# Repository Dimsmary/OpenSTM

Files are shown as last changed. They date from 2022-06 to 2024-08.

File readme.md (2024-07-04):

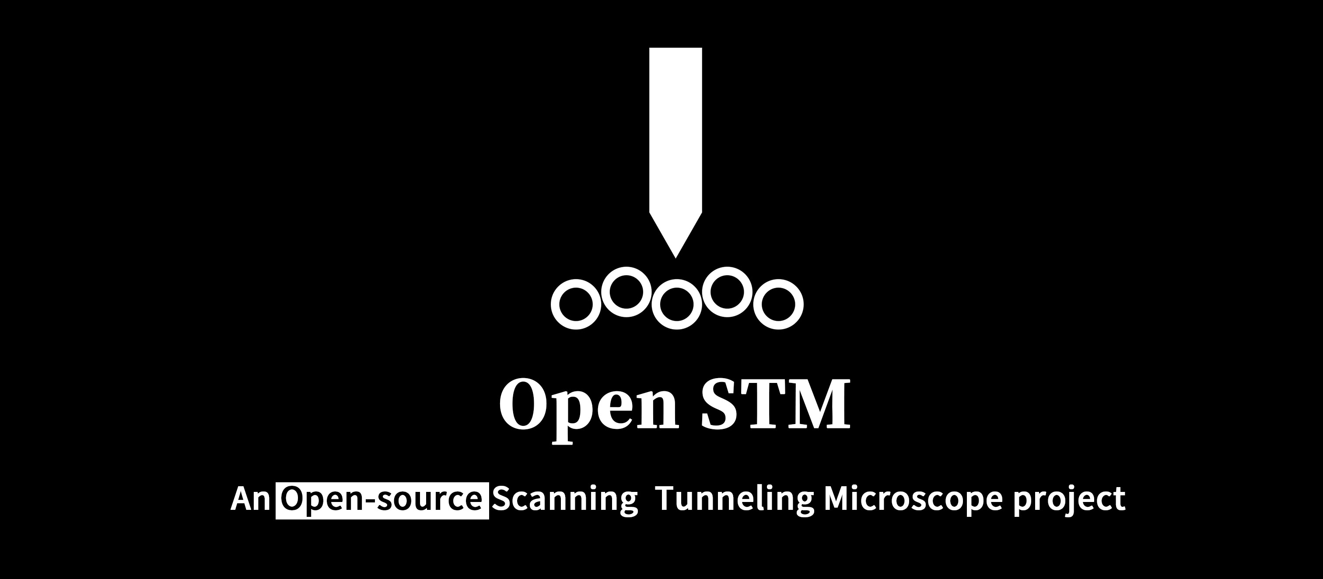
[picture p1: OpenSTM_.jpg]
OpenSTM_


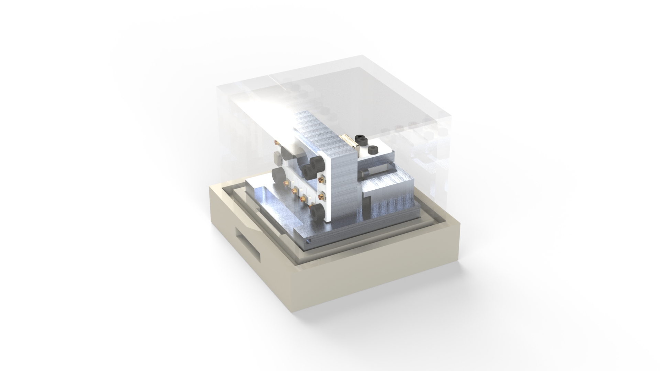
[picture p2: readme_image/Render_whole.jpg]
Render_whole


**[中文](readme.md) | [English](readme_eng.md)**

- [简介](#简介)
- [分支](#分支)
- [开源文件结构介绍](#开源文件结构介绍)
- [开发技术文档](#开发技术文档)
- [版本发布命名规则](#版本发布命名规则)
- [已发布的STM方案版本](#已发布的stm方案版本)
  - [<u>Release OpenSTM v1.0.0</u>](#urelease-openstm-v100u)
  - [<u>Release OpenSTM v2.0.0</u>](#urelease-openstm-v200u)
  - [<u>Release OpenSTM v3.0.0</u>](#urelease-openstm-v300u)
- [目前取得的成果](#目前取得的成果)
  - [隧穿距离-电流曲线](#隧穿距离-电流曲线)
  - [热解石墨（HOPG）的偏压-电流曲线](#热解石墨hopg的偏压-电流曲线)
  - [热解石墨（HOPG）原子成像](#热解石墨hopg原子成像)
- [联系我](#联系我)
- [赞助](#赞助)
- [开发记录](#开发记录)
- [致谢](#致谢)
- [参考工程](#参考工程)
- [主要参考文献](#主要参考文献)

# 简介

嗨，本项目是一个旨在通过DIY来搭建一个原子级扫描隧道显微镜。  

2022年6月，本项目已经成功测量了隧穿距离-电流曲线、热解石墨（HOPG）的偏压-电流曲线以及样品无尺寸定性成像。  

2023年5月，本项目成功扫描出热解石墨（HOPG）的碳原子。  

目前项目已经在科学开源硬件期刊《HardwareX》上发表，构建细节可参考论文内容。论文DOI：https://doi.org/10.1016/j.ohx.2023.e00504

# 分支

本仓库目前创建了两个分支，即[主分支](https://github.com/Dimsmary/OpenSTM/tree/main)(main)以及[文档分支](https://github.com/Dimsmary/OpenSTM/tree/Ref-Document)(Ref-Document)。主分支中放置了源代码等工程设计文件，文档分支放置了开发过程中参考的文档资料。之所以将这两部分分离是因为文档文件体积过于庞大所导致的。

# 开源文件结构介绍

- 3DModels

  包括**外壳设计文件**以及**CNC加工所需的STEP文件** 。

- Docs

  该目录下的文档包括了**项目概要**以及**显微镜构建指南**。
  
- Hardware
  
  包括使用ESP32 IDF编写的**单片机程序工程文件**（使用Platform IO），以及对应**固件**。
  注意！Platform IO的Platforms-Espressif 32版本应选择6.0.0，否则可能无法通过编译。

- PCB

  嘉立创EDA绘制的**PCB文件**，需要使用嘉立创EDA专业版打开。或直接在OSHW-Hub在线浏览（详见电路部分），移步[OSHWHUB](https://oshwhub.com/Dimsmary/4ieRpV8S00kGn1MTpsc4MyZat8MwQPzn)，点击右上方的“编辑器打开”。

- PythonScript  
  显微镜的上位机程序，具体使用方法参考**显微镜构建指南**。

# 开发技术文档

文档已发布在Arxiv: https://arxiv.org/abs/2310.05413, 你也可以在doc文件夹中寻找到。

# 版本发布命名规则

截至2023/10，目前已公布了三个不同机械结构的STM方案 ，其中V3.0.0版本已经可以实现STM的基本功能。

本项目将参考软件发行的方式，在STM方案更新后，采用Release的方式对方案进行发布，每次发布的STM方案版本号命名规则如下：

版本号以**A.B.C**式命名，当方案机械结构存在重构时，A将发生变化。在方案的电路、软件、机械结构存在较大的修改时，B将发生变化。当方案存在细微修改时，C将发生变化。

以1.0.0为例，该版本号即代表第一代机械结构的STM设计方案。

# 已发布的STM方案版本

## [<u>Release OpenSTM v1.0.0</u>](https://github.com/Dimsmary/OpenSTM/releases/tag/v1.0.0)

这是初代STM方案，机械结构采用两块铝板搭建：[<u>你，亲眼看过原子吗？ - 哔哩哔哩</u>](https://www.bilibili.com/video/BV1Jr4y1v7gq)  

方案较为简单，没有取得能够用于分析的实验结果，但后续方案的搭建基于本初代方案进行搭建，本版本的方案仅供参考，暂不提供详细的文档资料。  
发布的方案文件包括了：

- 3D模型文件（SolidWorks）
- Arduino程序：用于控制STM的ESP32单片机控制程序（采用LVGL进行交互）、基于MPU9250的震动探测程序，均采用Arduino+Platform IO进行开发
- PCB及原理图
- 用于测量干涉条纹的Python脚本
- LTSpice对电源芯片的仿真文件

## [<u>Release OpenSTM v2.0.0</u>](https://github.com/Dimsmary/OpenSTM/releases/tag/v2.0.0)

该版本方案为第二代显微镜结构：  [<u>耗时九个月，我可能来到了纳米尺度...... - 哔哩哔哩</u>](https://www.bilibili.com/video/BV1eB4y1S7u8)

该方案的结构能够测量：

- 隧穿距离-电流曲线
- 扫描隧道谱（STS）

v2.0.0.zip内含的文件包括：

- 3DModel：SolidWorks绘制的3D模型文件、CNC加工所需的STEP文件
- PCB：立创EDA专业版绘制的原理图、PCB文件
- Software：在Arduino文件夹下，包含ESP32单片机的控制程序、ATMEGA 328P单片机的控制程序。在Python文件夹下，包含了上位机控制软件、图像转换程序

## [<u>Release OpenSTM v3.0.0</u>](https://github.com/Dimsmary/OpenSTM/releases/tag/v3.0.0)

第三代扫描隧道显微镜，功能基本完善的一个版本，能够完成基本的曲线测量以及HOPG原子成像。
视频：https://www.bilibili.com/video/BV1TN411r7jG
复刻论文手稿：https://arxiv.org/abs/2310.05413
详细内容请参考手稿。

# 目前取得的成果

## 隧穿距离-电流曲线

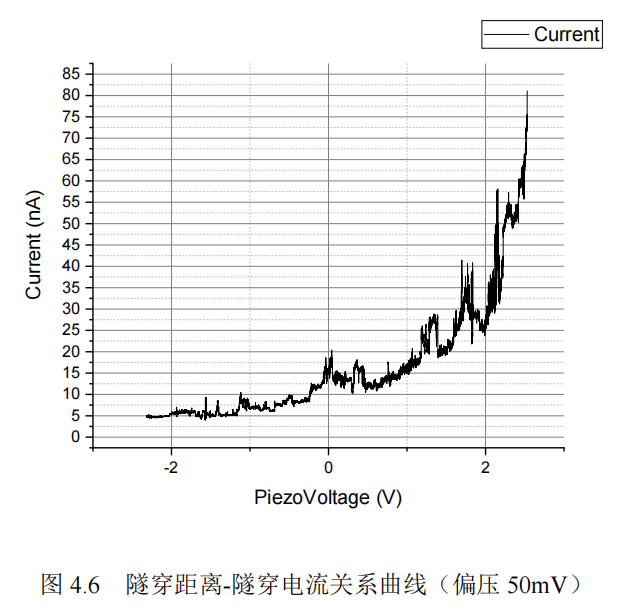
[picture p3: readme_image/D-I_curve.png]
D-I_curve
  

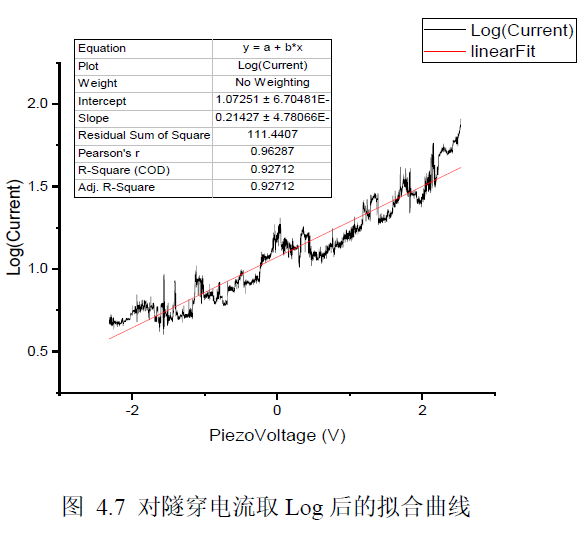
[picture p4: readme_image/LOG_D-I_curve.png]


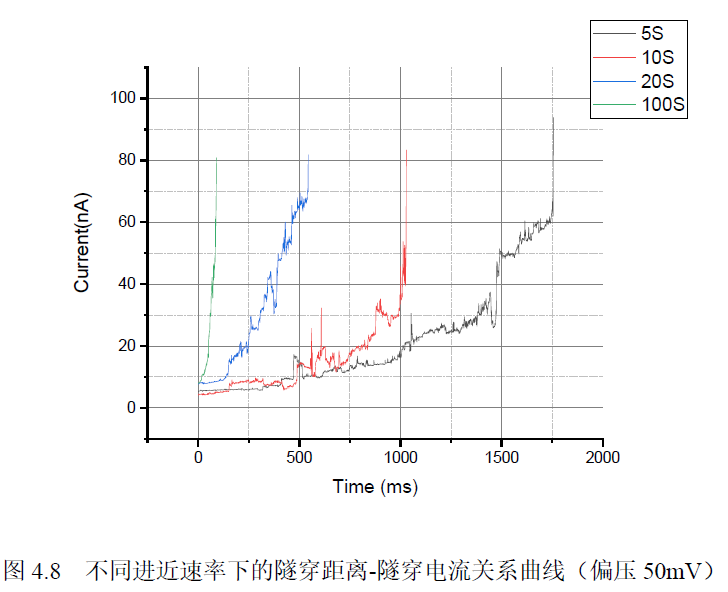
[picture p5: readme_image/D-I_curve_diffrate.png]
D-I_curve_diffrate
  

## 热解石墨（HOPG）的偏压-电流曲线

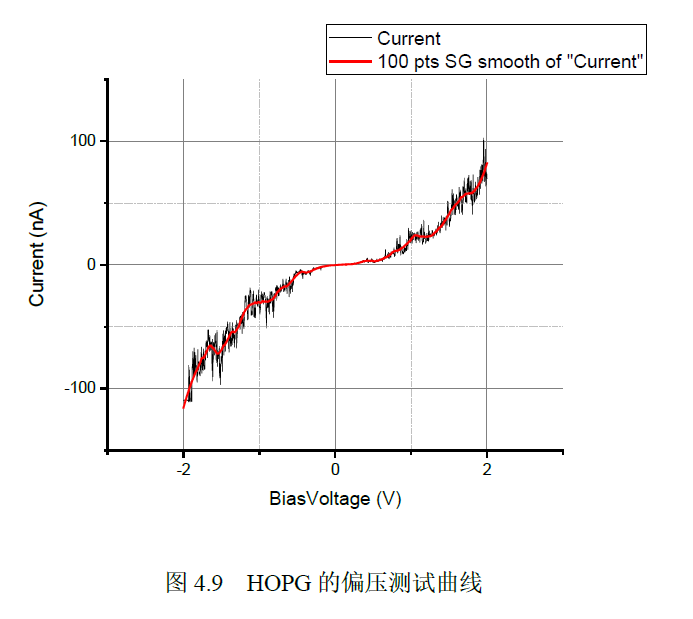
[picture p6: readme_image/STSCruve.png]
STSCruve


## 热解石墨（HOPG）原子成像

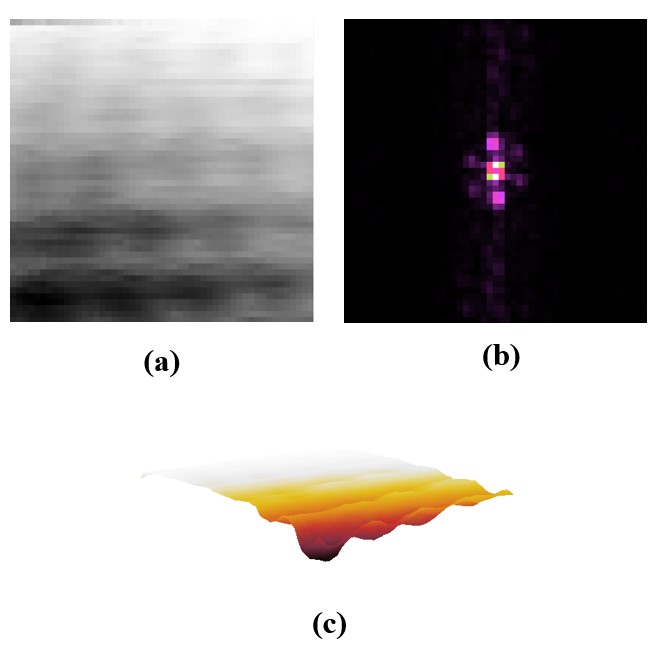
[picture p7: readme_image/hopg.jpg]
hopg


# 联系我

  如果你也想制作一个STM显微镜，或者对我有什么建议的话，可以在此页面提交Issue。

# 赞助

如果你喜欢本项目，欢迎在爱发电对我进行赞助：https://afdian.net/a/dimsmary

赞助可获得概述中文版一份。（虽然复刻指南已经发布在了Arxiv，但这里还是有一份中文省流版；
这份文档是对项目的一个概述，相较于readme更为详细，但复刻还是要参考Arxiv论文）

# 开发记录

- 2021/11
  
  不稳定隧穿

- 2022/1/11
  
  开源页面提交

- 2022/1/18
  
  减震台下加装了<网球>，减震效果拔群

- 2022/2/05
  
  1）系统模拟部分供电改为9V电池供电，数字部分继续使用开关电源。  
  2）ADP5070不工作了，奶奶的！为什么。  
  3）在《 Construction of a scanning tunneling microscope for imaging of carbon nanotubes》P35中发现隧穿电流应在100pA - 10nA，按照现有运放的倍数应该关注1V以内的信号，之前看样子搞错了。  
  4）OPA627的 ~~开环电压增益有120dB，~~ 输入偏置电流1pA，讲道理用100MΩ的反馈电阻应该是可行的？  

- 2022/2/16  
  
  对运放的输入输出特性进行了测试，证明前级隧道电流放大电路是可行的。

- 2022/3/14  
  
  1）CNC加工的新结构加工完成  
  2）摒弃LVGL与显示屏作为控制系统  

- 2022/3/21  
  
  使用了新的结构系统、电路、控制系统进行了隧穿电流进近测试：  
  1）隧穿电流初步稳定，能够维持十几秒。  
  2）通过八个点的采样测试隧穿电流-压电陶瓷形变曲线发现基本符合指数特征。  
  3）确认并不需要非常复杂的减震系统。  
  4）基本确认之前出现的输出跳动现象为热膨胀的失配。

- 2022/4/12  
  
  1）在对进近机械结构中的步进电机进行热隔离调整后，隧穿电流已非常稳定，能够维持至少30分钟。  
  2）对新的隧穿曲线进行分析，发现电流-压电陶瓷形变关系并不只是单纯的指数关系，结合老师给出的意见，怀疑有其他函数复合。初步怀疑为针尖与样品间形成的电容器导致的。  
  3）完善了细进近控制算法，现在可以点击开始进近之后去打几把极地大乱斗。  
  4）模拟部分供电由9V电池供电更换为3S锂聚合物电池供电。

- 2022/4/20  
  完成恒高模式下的STM图像扫描，并经过重复性实验验证，但无法确定图像尺度以及成像内容的完全可靠。

- 2022/5/01  
  攥写毕业设计论文。

- 2022/5/04  
  毕业设计论文攥写完成70%，开始编写恒流扫描算法。  

- 2022/6/16  
  第二代显微镜开源资料公布  

- 2022/10/21
  
  开始设计粘滑压电马达

- 2022/10/26
  
  完善技术文档
  
- 2023/1/4
  第三代电路、机械结构重构完成，粘滑压电马达设计完成，进入调试阶段（目前未发布，待验证后发布）。
  
  （1）电路电源方面：重构后的电路采用ADP5070搭配低噪声LDO的方案提供多个电源轨道（双±12V、5V），ADP5070采用紫米35W双C口电源适配器进行5V供电（原因在于该电源纹波极低，峰峰值在13mV左右，呈现为锯齿状）。
  
  （2）PCB板层设计方面：新一代电路板分为三块：电源板、MCU板、控制板。电源线在板之间采用同轴信号线连接，数据线采用IDC排线连接。
  
  （3）电路改进方面：MCU板继续沿用ESP32作为控制器，但模组型号更新为ESP32-S3，并留有WIFI天线挖槽，为日后升级做准备。控制板沿用第二代大部分设计保持不变，继续使用AD5761+OPA2227的方案对扫描头进行控制，但由于压电滑台的引入，控制板额外添加了AD8761作为对样品施加偏压的DAC，原本用于施加偏压的DAC现用于控制压电滑台。
  
  （4）机械结构设计方面：新一代机械结构整体尺寸缩小，并引入了粘-滑压电滑台进行粗进近（参考文章《Open-source XYZ nanopositioner for high-precision analytical applications》），并对前级放大器进行了金属全包裹屏蔽，进一步降低噪声耦合。
  
- 2023/1/18

  MCU模组更换为ESP32-WROOM-32E，S3模组的编译出现了一些问题，资料较少暂时无法解决。
  
  另外，为了提升MCU的效率，将开发框架从Arduino变更为ESP-IDF（从简单的GPIO翻转代码中发现，Platform IO + Arduino速度为800Khz，Arduino IDE为1.2Mhz，Platform IO + ESP-IDF为1.44Mhz）。
  
- 2023/2/12
  
  第三代电路、机械结构修改、验证完成。
  
  目前正在重构上位机、控制程序，截止目前已实现探针进近的PID控制，电流相较于上一代设计更加稳定，温漂问题得到很大程度改善。
  
- 2023/03/31
  
  1）发现了一些在压电滑台组装时遇到的问题：虽然压电滑台组装难度不高，但滑台在安装时需要与施加压力的磁铁保持一定程度的平行，否则压电滑台将无法长距离工作。
  
  2）拟设计两种压电滑台结构以适配不同形状的压电陶瓷
  
  3）软件完成D-I曲线测试以及偏压测试功能
  
- 2023/05/02
  
  1）完成了对HOPG的扫描，可以观察到碳原子模糊的轮廓。
  
  2）发现了一个有趣的现象：在探测HOPG样品的过程中，探针接近完成后的隧穿电流将会产生波动（环境振动引起），若此时的探针锐度达到了原子级分辨率，隧穿电流的波动曲线将会被耦合进一个类正弦波的曲线，并且在撞针后，这个耦合将消失（确定不为市电干扰，其波动周期为1.4ms左右，且在撞针后会消失）。
  
  我认为这是因为探针在进入隧穿距离之后，在环境振动的带动下，探针的X/Y轴将随着振动而移动，形成“扫描”的效果，碳原子表面的起伏将导致电流的周期性变化。
  
- 2023/05/03
  
  观察到HOPG上碳原子清晰的轮廓

- 2023/10/10

  三代机HardwareX手稿发布在Arxiv上：https://arxiv.org/abs/2310.05413

# 致谢

**五邑大学以及五邑大学的老师们**

**深圳嘉立创科技集团股份有限公司**

**Jürgen Müller**

**Daniel Berard的STM开源工程**

**John D. Alexander的STM开源工程**

**中国科学院光电技术研究所**

**所有为本项目提供建议的哔哩哔哩朋友**

# 参考工程

[1] John Alexander: STM Project, http://web.archive.org/web/20121107205242/http://www.geocities.com/spm_stm/Project.html

[2] Dan Berard: Home-Built STM, https://dberard.com/home-built-stm/

[3] Jürgen Müller: Homebrew STM, http://www.e-basteln.de/other/stm/overview/

[4] NanoSurf: NaioSTM, https://www.nanosurf.com/en/products/naiostm-stm-for-nanoeducation

# 主要参考文献 

[1].  Binnig G, Rohrer H. Scanning tunneling microscope: U.S. Patent 4,343,993[P]. 1982-8-10.

[2].  Besocke K. An easily operable scanning tunneling microscope[J]. Surface Science, 1987, 181(1-2): 145-153.

[3].  Ellis M D. Construction of a scanning tunneling microscope for imaging of carbon nanotubes[D]. Texas Tech University, 1998.

[4].  Rogers B L, Shapter J G, Skinner W M, et al. A method for production of cheap, reliable pt–ir tips[J]. Review of Scientific Instruments, 2000, 71(4): 1702-1705.

[5].  王琦. 高稳定扫描隧道显微镜的研制与应用[D].  中国科学技术大学,2014.

[6].  Petersen J P, Kandel S A. Circuit design considerations for current preamplifiers for scanning tunneling microscopy[J]. 2017.

[7].  Lounis S. Theory of scanning tunneling microscopy[J]. arXiv preprint arXiv:1404.0961, 2014.

[8].  Purdue University. TEM Pictures of STM Tips[EB/OL]. 2002[2022-9-20]. https://www.physics.purdue.edu/nanophys/uhvstm/tip.html.

[9].  Bai C. Scanning tunneling microscopy and its application[M]. Springer Science & Business Media, 2000.

[10].  Nasrollahzadeh M, Sajadi M S, Atarod M, et al. An introduction to green nanotechnology[M]. Academic Press, 2019:199-322.

[11].  Baird D, Shew A. Probing the history of scanning tunneling microscopy[J]. Discovering the nanoscale, 2004, 2: 145-156.

[12].  Merzbacher E. Quantum mechanics[M]. Jones & Bartlett Publishers, 1961.

[13].  曾谨言. 量子力学导论[M]. 第二版. 北京大学出版社, 2001.

[14].  Grafstrom S, Kowalski J, Neumann R. Design and detailed analysis of a scanning tunnelling microscope[J]. Measurement Science and Technology, 1990, 1(2): 139.

[15].  Nam A J, Teren A, Lusby T A, et al. Benign making of sharp tips for STM and FIM: Pt, Ir, Au, Pd, and Rh[J]. Journal of Vacuum Science & Technology B: Microelectronics and Nanometer Structures Processing, Measurement, and Phenomena, 1995, 13(4): 1556-1559.

[16].  Hahn J R, Hong Y A, Kang H. Electron tunneling across an interfacial water layer inside an STM junction: tunneling distance, barrier height and water polarization effect[J]. Applied Physics A, 1998, 66(1): S467-S472.

[17]. Woo D H, Choi E M, Yoon Y H, et al. Current–distance–voltage characteristics of electron tunneling through an electrochemical STM junction[J]. Surface science, 2007, 601(6): 1554-1559.

[18]. Alexander J D, Tortonese M, Nguyen T. Atomic force microscope with integrated optics for attachment to optical microscope: U.S. Patent 5,952,657[P]. 1999-9-14.

[19]. 陈大任,李国荣,殷庆瑞.逆压电效应的压电常数和压电陶瓷微位移驱动器[J].无机材料学报,1997(06):861-866.

[20]. Fialka J, Benes P, Michlovska L, et al. Measurement of thermal depolarization effects in piezoelectric coefficients of soft PZT ceramics via the frequency and direct methods[J]. Journal of the European Ceramic Society, 2016, 36(11): 2727-2738.

[21]. Instrumentation reference book[M]. Butterworth-Heinemann, 2009.

[22]. Lanza di Scalea F. Measurement of thermal expansion coefficients of composites using strain gages[J]. Experimental mechanics, 1998, 38(4): 233-241.

[23]. Wijnen B, Sanders P, Pearce J M. Improved model and experimental validation of deformation in fused filament fabrication of polylactic acid[J]. Progress in Additive Manufacturing, 2018, 3(4): 193-203.

[24]. Oliva A I, Aguilar M, Sosa V. Low-and high-frequency vibration isolation for scanning probe microscopy[J]. Measurement Science and Technology, 1998, 9(3): 383.

[25]. Okano M, Kajimura K, Wakiyama S, et al. Vibration isolation for scanning tunneling microscopy[J]. Journal of Vacuum Science & Technology A: Vacuum, Surfaces, and Films, 1987, 5(6): 3313-3320.

[26]. Walzer K, Sternberg M, Hietschold M. Formation and characterization of coronene monolayers on HOPG (0001) and MoS2 (0001): a combined STM/STS and tight-binding study[J]. Surface science, 1998, 415(3): 376-384.

[27]. Kusunoki K, Sakata I, Miyamura K. Interaction between Tip and HOPG Surface Studied by STS[C]//Analytical Sciences/Supplements Proceedings of IUPAC International Congress on Analytical Sciences 2001 (ICAS 2001). The Japan Society for Analytical Chemistry, 2002: i1267-i1268.

[28]. Chen C J. Theory of scanning tunneling spectroscopy[J]. Journal of Vacuum Science & Technology A: Vacuum, Surfaces, and Films, 1988, 6(2): 319-322.

[29]. El Abedin S Z, Borissenko N, Endres F. Electrodeposition of nanoscale silicon in a room temperature ionic liquid[J]. Electrochemistry communications, 2004, 6(5): 510-514.

[30]. Walzer K, Hietschold M. STM and STS investigation of ultrathin tin phthalocyanine layers adsorbed on HOPG (0001) and Au (111)[J]. Surface science, 2001, 471(1-3): 1-10.

[31].  Liao H S, Werner C, Slipets R, et al. Low-cost, open-source XYZ nanopositioner for high-precision analytical applications[J]. HardwareX, 2022: e00317.

[32]. De Voogd J M, Van Spronsen M A, Kalff F E, et al. Fast and reliable pre-approach for scanning probe microscopes based on tip-sample capacitance[J]. Ultramicroscopy, 2017, 181: 61-69.

[33]. Wallash A J, Levit L. Electrical breakdown and ESD phenomena for devices with nanometer-to-micron gaps[C]//Reliability, Testing, and Characterization of MEMS/MOEMS Ii. SPIE, 2003, 4980: 87-96.

[34]. Gao C, Kuhlmann-Wilsdorf D, Makel D D. The dynamic analysis of stick-slip motion[J]. Wear, 1994, 173(1-2): 1-12.

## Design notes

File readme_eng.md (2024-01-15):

OpenSTM_

Render_whole

**[中文](readme.md) | [English](readme_eng.md)**

# Introduction

Hi, this is a DIY STM(Scanning Tunneling Microscope) project!

In June 2022: the distance-tunneling current curve, and bias voltage-tunneling current curve of HOPG were measured.

In May 2023, the image of HOPG in atom resolution was obtained.

**This project has been published on HardWareX, all the details can be found in the article. DOI:  https://doi.org/10.1016/j.ohx.2023.e00504**

# Branches

Currently, the repository has two branches: [main ](https://github.com/Dimsmary/OpenSTM/tree/main)and [Ref-Document](https://github.com/Dimsmary/OpenSTM/tree/Ref-Document).

The open-source file was included in the main, and the references(datasheet, paper, etc.) documents were in the Ref-Documents branches. Since the documents file occupies a large amount of space, I have to separate the documents file into another branch.

# File Structure

- 3DModels

  Included **design file of structure** and **STEP file for CNC**

- Docs

  Included **project introduction** and **build tutorial**
  
- Hardware
  
  **MCU source code**(by ESP-IDF and Platform IO) and **firmware**

- PCB

  PCB file(Easy EDA), browsing online: [OSHWHUB](https://oshwhub.com/Dimsmary/4ieRpV8S00kGn1MTpsc4MyZat8MwQPzn)

- PythonScript  
  
  Control software code

# Document

The document has been published on Arxiv: https://arxiv.org/abs/2310.05413, and you can also find it in the doc folder.

# Version Release Naming Rules

As of October 2023, three different mechanical structures for the STM (Scanning Tunneling Microscope) have been published, with version 3.0.0 capable of basic STM functionality.

This project will follow the software release approach, where after each update in the STM design, a release will be made. The version numbering for each released STM design will follow the following format:

The version number will be in the format of **A.B.C**. When there is a significant reconstruction of the mechanical structure, A will change. When there are substantial changes to the circuitry, software, or mechanical structure of the design, B will change. When there are minor modifications to the design, C will change.

For example, 1.0.0 represents the first-generation mechanical structure design of the STM.

# Releases

## [<u>Release OpenSTM v1.0.0</u>](https://github.com/Dimsmary/OpenSTM/releases/tag/v1.0.0)

This is the first-generation STM (Scanning Tunneling Microscope) design, constructed using two aluminum plates. You can view it here: https://www.youtube.com/watch?v=NZt7yUdhfqY

This design is relatively simple and did not yield experimental results suitable for analysis. However, subsequent designs are built upon this first-generation design. This version of the design is provided for reference only and does not currently include detailed documentation.

The released design files include:

- 3D model files (SolidWorks).
- Arduino programs: These programs control the STM and include the ESP32 microcontroller control program (using LVGL for interaction) and a vibration detection program based on the MPU9250. Both were developed using Arduino and Platform IO.
- PCB and schematic files.
- Python scripts for measuring interference fringes.
- LTSpice simulation files for the power supply chip.

## [<u>Release OpenSTM v2.0.0</u>](https://github.com/Dimsmary/OpenSTM/releases/tag/v2.0.0)

This version of the design represents the second-generation microscope structure. You can view it here: https://www.youtube.com/watch?v=2gPIJrTNqIA

The structure of this design allows for the measurement of:

- Tunneling distance-current curves.
- Scanning Tunneling Spectroscopy (STS).

The files included in v2.0.0.zip are:

- 3DModel: 3D model files drawn in SolidWorks and STEP files required for CNC machining.
- PCB: Schematics and PCB files drawn using the professional version of Jialichuang EDA.
- Software: In the Arduino folder, it includes control programs for the ESP32 microcontroller and the ATMEGA 328P microcontroller. In the Python folder, it contains the upper-level control software and image conversion programs.

## [Release OpenSTM v3.0.0](https://github.com/Dimsmary/OpenSTM/releases/tag/v3.0.0)

This is the third-generation scanning tunneling microscope, a version with basic functionality that can perform curve measurements and HOPG atomic imaging. Video: https://www.youtube.com/watch?v=noWLMcfyqbQ Replication paper manuscript: https://arxiv.org/abs/2310.05413 For detailed information, please refer to the manuscript.

# Results

## Distance-tunneling current curve

D-I_curve  



D-I_curve_diffrate  

## Bias voltage-tunneling current curve of HOPG

STSCruve

## Atom image of HOPG

hopg

# Contact me

If you would like to build an STM microscope yourself or have any suggestions for me, you can submit an issue on this page.

# Development Record

- November 2021

  Unstable tunneling.

- January 11, 2022

  Submission of the open-source page.

- January 18, 2022

  Added tennis balls under the vibration isolation table, significantly improving vibration isolation.

- February 05, 2022

  1. Changed the power supply for the system simulation part to 9V battery while continuing to use a switch power supply for the digital part.
  2. ADP5070 stopped working. Frustrating!
  3. Discovered that tunneling current should be between 100pA - 10nA, which suggests signals within 1V for the existing op-amps, realizing previous mistakes.s
  4. OPA627 has an open-loop voltage gain of 120dB and input bias current of 1pA, making it reasonable to use a 100MΩ feedback resistor?

- February 16, 2022

  Tested the input-output characteristics of the op-amp, confirming the feasibility of the front-end tunnel current amplification circuit.

- March 14, 2022

  1. Completed CNC machining for the new structural design.
  2. Abandoned LVGL and display as the control system.

- March 21, 2022

  Conducted tunnel current approach tests using the new structural system, circuit, and control system:

  1. Tunnel current is initially stable and can be maintained for about ten seconds.
  2. Found that the tunnel current-piezoelectric ceramic deformation curve, sampled at eight points, generally follows exponential characteristics.
  3. Confirmed that a complex vibration isolation system is not required.
  4. Essentially confirmed that the previous output jumping phenomenon was due to thermal expansion mismatch.

- April 12, 2022

  1. Tunnel current has become very stable after adjusting the heat isolation of the stepping motor in the approach mechanical structure. It can now be maintained for at least 30 minutes.
  2. Analyzed the new tunneling curve and suspected that the current-piezoelectric ceramic deformation relationship is not purely exponential. It might be due to the formation of a capacitor between the tip and the sample.
  3. Improved the fine approach control algorithm, allowing you to engage in polar battles after clicking "start approach."
  4. Changed the power supply for the simulation part from a 9V battery to a 3S lithium-polymer battery.

- April 20, 2022

  Completed STM image scanning in constant height mode and verified it through repeated experiments, but could not reliably determine the image scale and content.

- May 01, 2022

  Started writing the graduation thesis.

- May 04, 2022

  70% of the graduation thesis writing is complete, began writing the constant current scanning algorithm.

- June 16, 2022

  Released open-source materials for the second-generation microscope.

- October 21, 2022

  Started designing stick-slip piezoelectric motors.

- October 26, 2022

  Improved technical documentation.

- January 4, 2023

  Completed the reconstruction of the third-generation circuit and mechanical structure, designed the stick-slip piezoelectric motor, and entered the debugging phase (not yet released, pending validation).

  (1) Regarding circuit power supply: The reconstructed circuit uses the ADP5070 with a low-noise LDO scheme to provide multiple power rails (dual ±12V, 5V). The ADP5070 is powered by a 35W dual-C port power adapter with extremely low ripple (peaking at around 13mV, resembling a sawtooth wave).

  (2) Regarding PCB layer design: The new generation circuit board is divided into three parts: power board, MCU board, and control board. Coaxial signal lines are used for connections between the boards, while IDC ribbon cables are used for data lines.

  (3) Regarding circuit improvements: The MCU board continues to use ESP32 as the controller, but the module model is updated to ESP32-S3, with a slot reserved for a WIFI antenna for future upgrades. The control board largely maintains the design of the second generation, continuing to use the AD5761+OPA2227 scheme to control the scanning head. However, due to the introduction of the piezoelectric slide stage, the control board adds an AD8761 as a DAC to apply bias voltage to the sample, repurposing the originally used DAC for biasing to control the piezoelectric slide stage.

  (4) Regarding mechanical structure design: The new generation mechanical structure has reduced overall dimensions and introduced a stick-slip piezoelectric slide stage for coarse approach (referencing the article "Open-source XYZ nanopositioner for high-precision analytical applications"). Additionally, the front-end amplifier has been further shielded with full metal wrapping to further reduce noise coupling.

- January 18, 2023

  The MCU module was changed to ESP32-WROOM-32E, and some issues arose with the S3 module that currently cannot be resolved due to limited documentation. To improve MCU efficiency, the development framework was changed from Arduino to ESP-IDF (simple GPIO code flipping revealed that Platform IO + Arduino runs at 800KHz, Arduino IDE at 1.2MHz, and Platform IO + ESP-IDF at 1.44MHz).

- February 12, 2023

  Completed modifications and validation of the third-generation circuit, mechanical structure, and testing are ongoing. Currently, PID control for probe approach has been implemented, resulting in more stable current compared to the previous generation, and a significant improvement in thermal drift issues.

- March 31, 2023

  1. Encountered some issues during the assembly of the piezoelectric slide stage: Although the assembly difficulty of the piezoelectric slide stage is not high, the slide stage needs to be kept somewhat parallel to the magnet applying pressure during installation; otherwise, the piezoelectric slide stage will not work over long distances.
  2. Planning to design two piezoelectric slide stage structures to adapt to different shapes of piezoelectric ceramics.
  3. Software completed D-I curve testing and bias testing functionality.

- May 02, 2023

  1. Completed scanning of HOPG, and observed the blurred outline of carbon atoms.
  2. Discovered an interesting phenomenon: during the detection of HOPG samples, the tunneling current will fluctuate as the probe approaches (caused by environmental vibrations). If the sharpness of the probe reaches atomic resolution at this time, the fluctuation curve of the tunneling current will be coupled into a sinusoidal-like curve, and this coupling will disappear after a collision with the sample (confirmed not to be interference from the power grid, with a fluctuation period of about 1.4ms and disappearing after a probe collision).

  I believe this is because after entering the tunneling distance, the probe's X/Y axis moves with the vibration caused by environmental vibrations, creating a "scanning" effect, and the undulations on the carbon atom surface lead to periodic variations in current.

- May 03, 2023

  Observed clear outlines of carbon atoms on HOPG.

- October 10, 2023

  The HardwareX manuscript for the third-generation hardware has been published on Arxiv: https://arxiv.org/abs/2310.05413.
# Acknowledgement

**Wuyi University and Teachers**

**JLC PCB and Easy EDA Team**

**Jürgen Müller**

**Daniel Berard's Project'**

**John D. Alexander's Project**

**Institude of Optics and Electronics, Chinese Academy of Sciences**

**All friends from Bilibili**

# Reference Project

[1] John Alexander: STM Project, http://web.archive.org/web/20121107205242/http://www.geocities.com/spm_stm/Project.html

[2] Dan Berard: Home-Built STM, https://dberard.com/home-built-stm/

[3] Jürgen Müller: Homebrew STM, http://www.e-basteln.de/other/stm/overview/

[4] NanoSurf: NaioSTM, https://www.nanosurf.com/en/products/naiostm-stm-for-nanoeducation

# Reference Paper

[1].  Binnig G, Rohrer H. Scanning tunneling microscope: U.S. Patent 4,343,993[P]. 1982-8-10.

[2].  Besocke K. An easily operable scanning tunneling microscope[J]. Surface Science, 1987, 181(1-2): 145-153.

[3].  Ellis M D. Construction of a scanning tunneling microscope for imaging of carbon nanotubes[D]. Texas Tech University, 1998.

[4].  Rogers B L, Shapter J G, Skinner W M, et al. A method for production of cheap, reliable pt–ir tips[J]. Review of Scientific Instruments, 2000, 71(4): 1702-1705.

[5].  王琦. 高稳定扫描隧道显微镜的研制与应用[D].  中国科学技术大学,2014.

[6].  Petersen J P, Kandel S A. Circuit design considerations for current preamplifiers for scanning tunneling microscopy[J]. 2017.

[7].  Lounis S. Theory of scanning tunneling microscopy[J]. arXiv preprint arXiv:1404.0961, 2014.

[8].  Purdue University. TEM Pictures of STM Tips[EB/OL]. 2002[2022-9-20]. https://www.physics.purdue.edu/nanophys/uhvstm/tip.html.

[9].  Bai C. Scanning tunneling microscopy and its application[M]. Springer Science & Business Media, 2000.

[10].  Nasrollahzadeh M, Sajadi M S, Atarod M, et al. An introduction to green nanotechnology[M]. Academic Press, 2019:199-322.

[11].  Baird D, Shew A. Probing the history of scanning tunneling microscopy[J]. Discovering the nanoscale, 2004, 2: 145-156.

[12].  Merzbacher E. Quantum mechanics[M]. Jones & Bartlett Publishers, 1961.

[13].  曾谨言. 量子力学导论[M]. 第二版. 北京大学出版社, 2001.

[14].  Grafstrom S, Kowalski J, Neumann R. Design and detailed analysis of a scanning tunnelling microscope[J]. Measurement Science and Technology, 1990, 1(2): 139.

[15].  Nam A J, Teren A, Lusby T A, et al. Benign making of sharp tips for STM and FIM: Pt, Ir, Au, Pd, and Rh[J]. Journal of Vacuum Science & Technology B: Microelectronics and Nanometer Structures Processing, Measurement, and Phenomena, 1995, 13(4): 1556-1559.

[16].  Hahn J R, Hong Y A, Kang H. Electron tunneling across an interfacial water layer inside an STM junction: tunneling distance, barrier height and water polarization effect[J]. Applied Physics A, 1998, 66(1): S467-S472.

[17]. Woo D H, Choi E M, Yoon Y H, et al. Current–distance–voltage characteristics of electron tunneling through an electrochemical STM junction[J]. Surface science, 2007, 601(6): 1554-1559.

[18]. Alexander J D, Tortonese M, Nguyen T. Atomic force microscope with integrated optics for attachment to optical microscope: U.S. Patent 5,952,657[P]. 1999-9-14.

[19]. 陈大任,李国荣,殷庆瑞.逆压电效应的压电常数和压电陶瓷微位移驱动器[J].无机材料学报,1997(06):861-866.

[20]. Fialka J, Benes P, Michlovska L, et al. Measurement of thermal depolarization effects in piezoelectric coefficients of soft PZT ceramics via the frequency and direct methods[J]. Journal of the European Ceramic Society, 2016, 36(11): 2727-2738.

[21]. Instrumentation reference book[M]. Butterworth-Heinemann, 2009.

[22]. Lanza di Scalea F. Measurement of thermal expansion coefficients of composites using strain gages[J]. Experimental mechanics, 1998, 38(4): 233-241.

[23]. Wijnen B, Sanders P, Pearce J M. Improved model and experimental validation of deformation in fused filament fabrication of polylactic acid[J]. Progress in Additive Manufacturing, 2018, 3(4): 193-203.

[24]. Oliva A I, Aguilar M, Sosa V. Low-and high-frequency vibration isolation for scanning probe microscopy[J]. Measurement Science and Technology, 1998, 9(3): 383.

[25]. Okano M, Kajimura K, Wakiyama S, et al. Vibration isolation for scanning tunneling microscopy[J]. Journal of Vacuum Science & Technology A: Vacuum, Surfaces, and Films, 1987, 5(6): 3313-3320.

[26]. Walzer K, Sternberg M, Hietschold M. Formation and characterization of coronene monolayers on HOPG (0001) and MoS2 (0001): a combined STM/STS and tight-binding study[J]. Surface science, 1998, 415(3): 376-384.

[27]. Kusunoki K, Sakata I, Miyamura K. Interaction between Tip and HOPG Surface Studied by STS[C]//Analytical Sciences/Supplements Proceedings of IUPAC International Congress on Analytical Sciences 2001 (ICAS 2001). The Japan Society for Analytical Chemistry, 2002: i1267-i1268.

[28]. Chen C J. Theory of scanning tunneling spectroscopy[J]. Journal of Vacuum Science & Technology A: Vacuum, Surfaces, and Films, 1988, 6(2): 319-322.

[29]. El Abedin S Z, Borissenko N, Endres F. Electrodeposition of nanoscale silicon in a room temperature ionic liquid[J]. Electrochemistry communications, 2004, 6(5): 510-514.

[30]. Walzer K, Hietschold M. STM and STS investigation of ultrathin tin phthalocyanine layers adsorbed on HOPG (0001) and Au (111)[J]. Surface science, 2001, 471(1-3): 1-10.

[31].  Liao H S, Werner C, Slipets R, et al. Low-cost, open-source XYZ nanopositioner for high-precision analytical applications[J]. HardwareX, 2022: e00317.

[32]. De Voogd J M, Van Spronsen M A, Kalff F E, et al. Fast and reliable pre-approach for scanning probe microscopes based on tip-sample capacitance[J]. Ultramicroscopy, 2017, 181: 61-69.

[33]. Wallash A J, Levit L. Electrical breakdown and ESD phenomena for devices with nanometer-to-micron gaps[C]//Reliability, Testing, and Characterization of MEMS/MOEMS Ii. SPIE, 2003, 4980: 87-96.

[34]. Gao C, Kuhlmann-Wilsdorf D, Makel D D. The dynamic analysis of stick-slip motion[J]. Wear, 1994, 173(1-2): 1-12.

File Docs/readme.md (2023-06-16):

*注意！本文档仅适用于2.0版本的设计，3.0的技术手册正在编写中。*

# 开发技术文档

## 简介

本文档介绍了当前版本下的STM构建、设计原理。

但由于目前STM设计的不完备性，不推荐对本项目进行完全的复现，但可以参考本项目已经验证后的设计。

### STM基础知识

- [STM原理基本概述](0-0-STMIntroduction.md)

- [STM基本结构](0-1-STMBasicStructure.md)

- [STM工作模式](0-2-STMWorkMode.md)

### 各组成部分设计

- [前级放大器设计](1-1-PreampDesign.md)

- [探针制作](1-2-Probe.md)

- [扫描头设计](1-3-ScanHead.md)

- [机械结构设计](1-4-MachenicalDesign.md)

- [控制电路设计](1-5-ControlCircuit.md)

- [减震系统设计](1-6-DampingSystem.md)

## 现阶段取得的数据

- [热失配估算](2-1-ThermalMismatch.md)

- [稳定性评估](2-2-StableTest.md)

- [隧穿距离-电流曲线](2-3-DistanceCurrentCurve.md)

- [偏压测试](2-4-BiasTest.md)

- [成像测试](2-5-ImageTest.md)

## 后续工作

- [粘-滑压电滑台设计](3-1-StickSlidePositionerDesign.md)

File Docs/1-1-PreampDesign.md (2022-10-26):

## 前级放大器设计

        隧穿电流大小在100pA~10nA[1]区间，故需要前级放大器具备可观的电流放大能力。本项目采用运算放大器（运放）作为核心放大元件，通过搭配反馈电阻构成跨组放大器对隧穿电流进行放大。

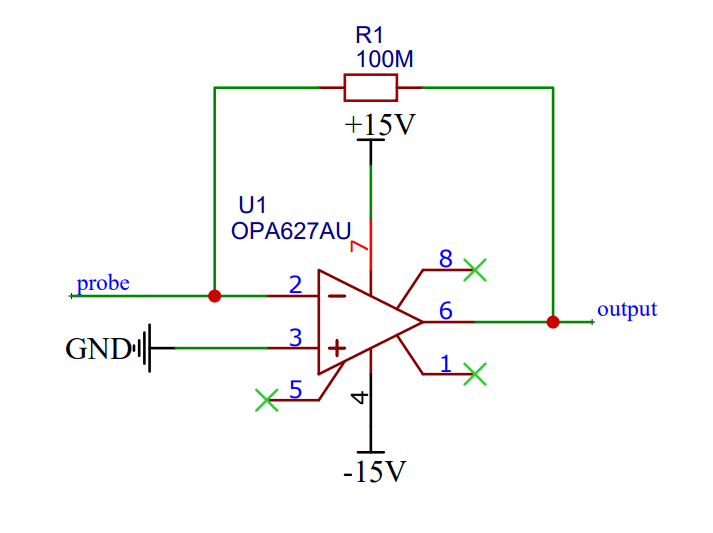
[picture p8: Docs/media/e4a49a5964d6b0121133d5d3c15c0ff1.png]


        图上为前级放大器的简化原理图，运放型号为德州仪器公司生产的OPA627，反馈电阻阻值为100×10^6 Ω即100MΩ。在选择运算放大器时主要关注输入偏置电流参数：OPA627的输入偏置电流典型值为1pA，即大小为隧穿电流最小值的1/100，偏置电流大小与最小隧穿电流大小相差两个数量级，满足对隧穿电流的测量条件。

        通过如图所示电路可以将端口probe处输入的隧穿电流转换电压信号在端口output处输出。通过运算放大器的特性可知，前级放大器的电流-电压转化公式为（其中，U_out为前级放大器的输出电压，R_1为反馈电阻阻值，I_Tunneling为隧穿电流，方向定义为从端口probe处流入）：

$$
U_{out}=-R_1 I_{Tunneling}
$$

        即电流-电压放大倍数由反馈电阻R1直接决定，在上图中，R1阻值为100MΩ，即放大倍数为10^8倍。可认为当存在10nA大小的隧穿电流输入至输入端时，该电流将被放大为-1V的电压在输出端输出。

# 放大性能简易验证

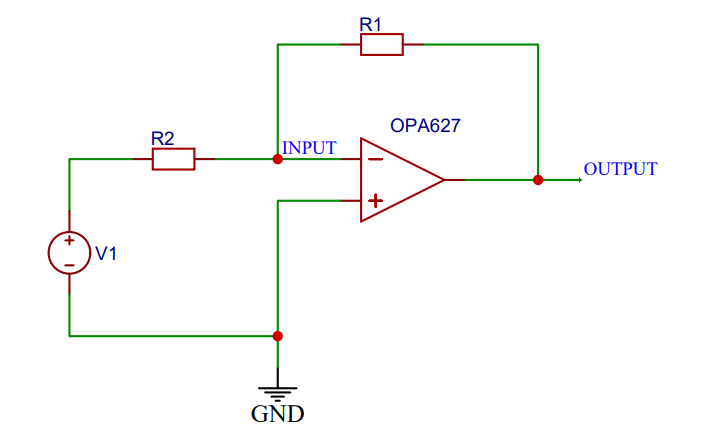
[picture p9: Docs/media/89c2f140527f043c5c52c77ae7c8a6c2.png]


        可变电压源V1经过阻值与R_1接近的大电阻R_2（范围在1MΩ~100MΩ）接入前级放大器的输入端，产生小电流。通过运算放大器的虚地特性可知，当运放的同相输入端接地时，反相输入端的电位也同时为地，则如图所示的测试电路中的前级放大器的输入电流可由公式(3.2)计算（其中U_V1为可变电压源输出电压，R_2为电阻阻值）：

$$
I_{INPUT}=\frac{U_{V1}}{R_2}
$$

        结合前级放大器的转换公式(3.1)，则此时可变电压源V1输出电压与前级放大器输出电压间的关系应为（其中R_1为前级放大器的反馈电阻阻值）：

$$
U_{OUTPUT}=-R_1×\frac{U_{V1}}{R_2}
$$

        若前级放大器性能良好，则在改变可变电压源V1的电压时，前级放大器的输出电压值应始终满足上述公式并拥有良好的线性度。

        在放大器性能验证中，测试将分为两组：两组测试的R_1均被设置为误差为±5%的100MΩ电阻，两组测试的R_2被分别设置为误差为±5%，阻值为1MΩ、100MΩ的电阻。测试将对可变电压源输出电压-前级放大器输出电压曲线进行测量，测量仪器为RIGOL-DS1102型示波器，测试结果如下：

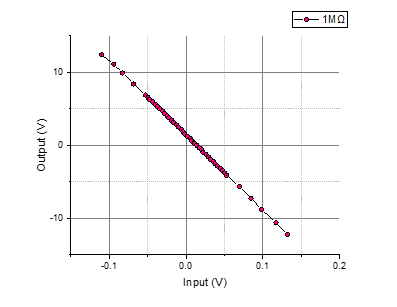
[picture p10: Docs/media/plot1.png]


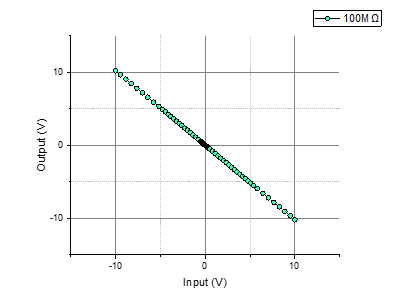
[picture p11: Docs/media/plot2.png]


# 参考资料

[1].    Ellis M D. Construction of a scanning tunneling microscope for imaging of carbon nanotubes[D]. Texas Tech University, 1998.

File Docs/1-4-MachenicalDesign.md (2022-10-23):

# 机械结构设计

## 设计总览

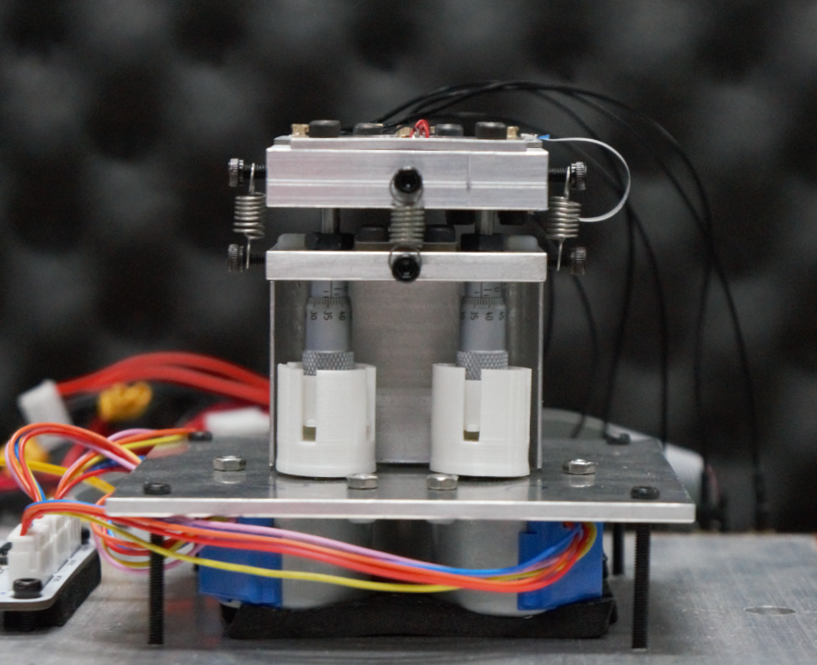
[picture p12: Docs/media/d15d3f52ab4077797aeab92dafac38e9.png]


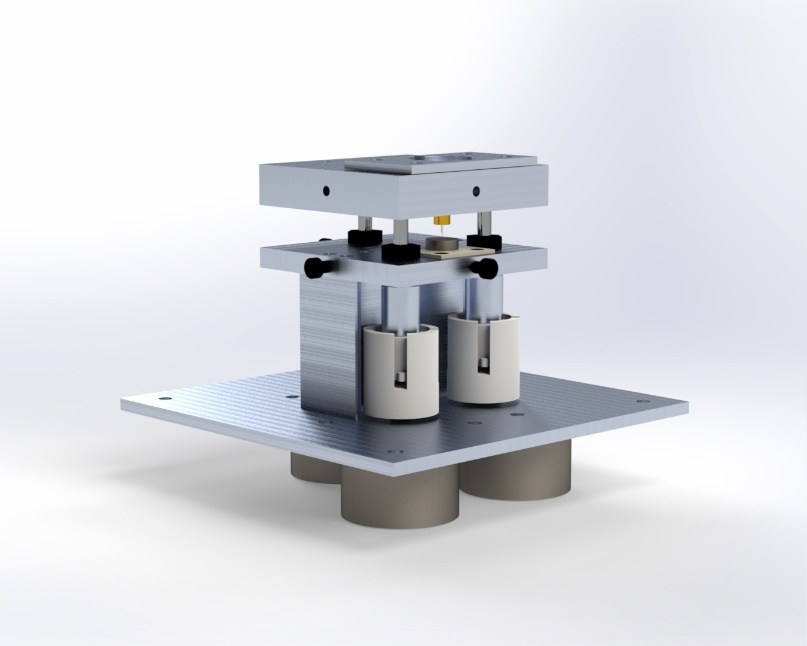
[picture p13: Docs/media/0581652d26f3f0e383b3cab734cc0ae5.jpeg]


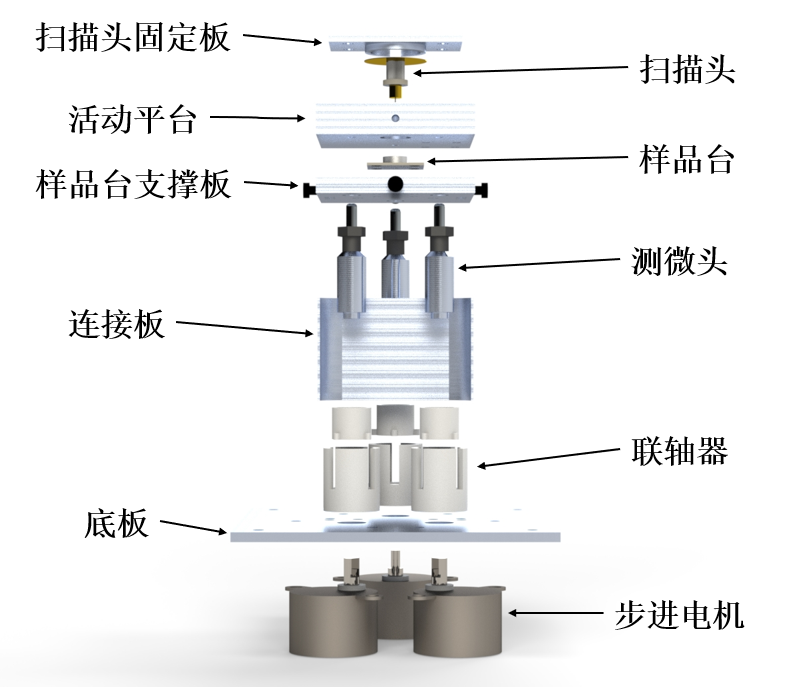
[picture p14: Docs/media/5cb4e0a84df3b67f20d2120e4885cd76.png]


        上图分别展示了显微镜的机械结构实物图、简化渲染示意图以及机械结构爆炸视图。
机械结构的各个组成部分如图所示，各个板材使用CNC进行加工成型，联轴器使用3D打印成型。扫描头固定板将扫描头固定于活动平台上，从而实现扫描头与活动平台同步运动。活动平台被三颗能够通过旋转实现伸缩的测微头顶起，从而实现三轴式的上下运动。活动平台与样品台支撑板之间通过拉簧连接以增加牢固性。测微头通过联轴器与步进电机连接，从而实现自动旋转伸缩。

        在系统工作时，除活动平台、扫描头固定板、扫描头外所有部件均为固定状态，活动平台可以经由步进电机联动的测微头控制，带动探针上下运动实现探针对样品的相对移动。

## 机械进近结构

        K. Besocke于1986年提出了一种能够简单操作的扫描隧道显微镜结构[1]，本项目基于其三轴进近结构进行改进，搭建了机械进近结构。

        机械进近结构由活动平台及其所承载的探针与微分头组成，活动平台与三个支撑微分头构成了一个三轴姿态调整装置。微分头、活动平台、探针的俯视关系如图3.19所示，活动平台为50×50cm的正方形铝块，其上钻有三个用于定位微分头的圆形凹槽A、B、C。探针、凹槽A的圆心位于B、C凹槽圆心的垂直平分线上，探针与B、C凹槽圆心的连线向凹槽A方向偏移了0.5mm。

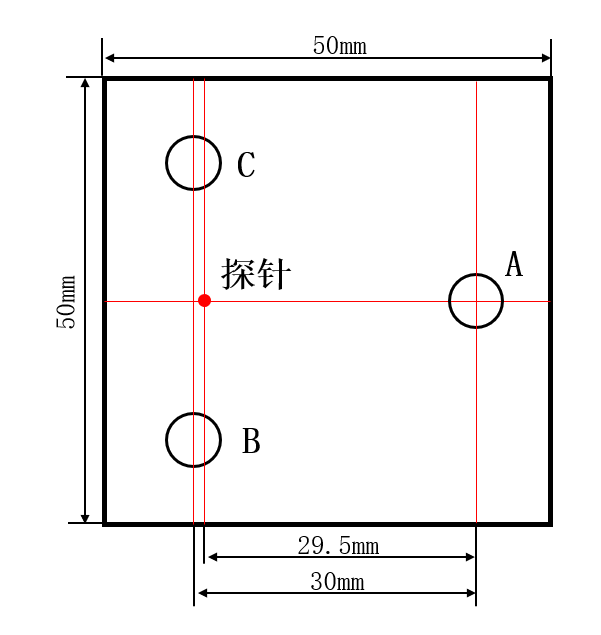
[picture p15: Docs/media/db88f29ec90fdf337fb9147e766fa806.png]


        当某一微分头上升或下降时，将带动活动平台在对应槽位方向发生俯仰运动。当微分头A、微分头B位置固定，微分头C向下运动一个单位时，由于探针在微分头B、C中间，通过相似三角形原理可计算出探针仅下降了1/2个单位，如图3.20所示。当微分头B、C位置固定，微分头A向下运动一个单位时，由于探针位于微分头A圆心与B、C圆心连线的1/60处，故探针仅向下运动了1/60个单位，如图所示。

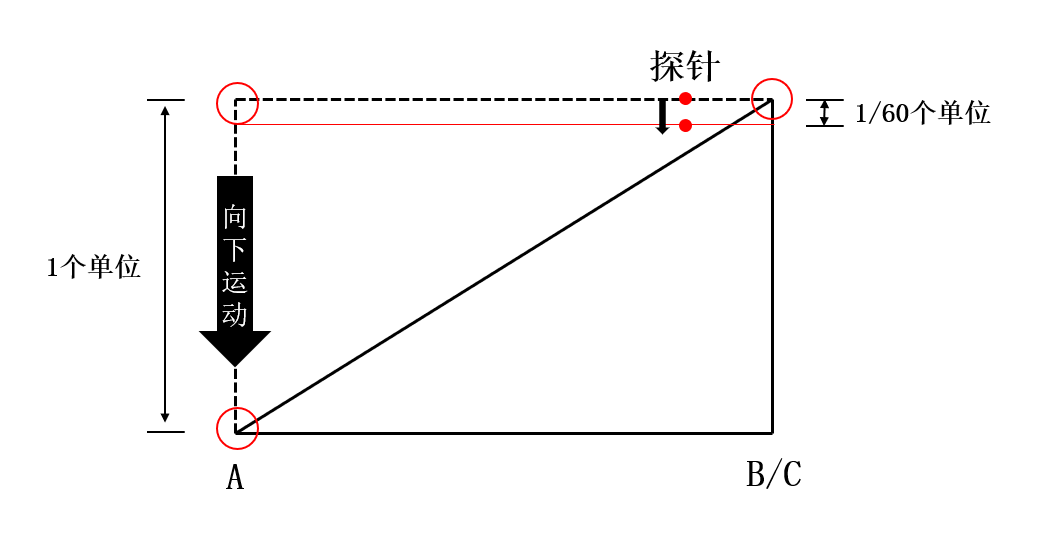
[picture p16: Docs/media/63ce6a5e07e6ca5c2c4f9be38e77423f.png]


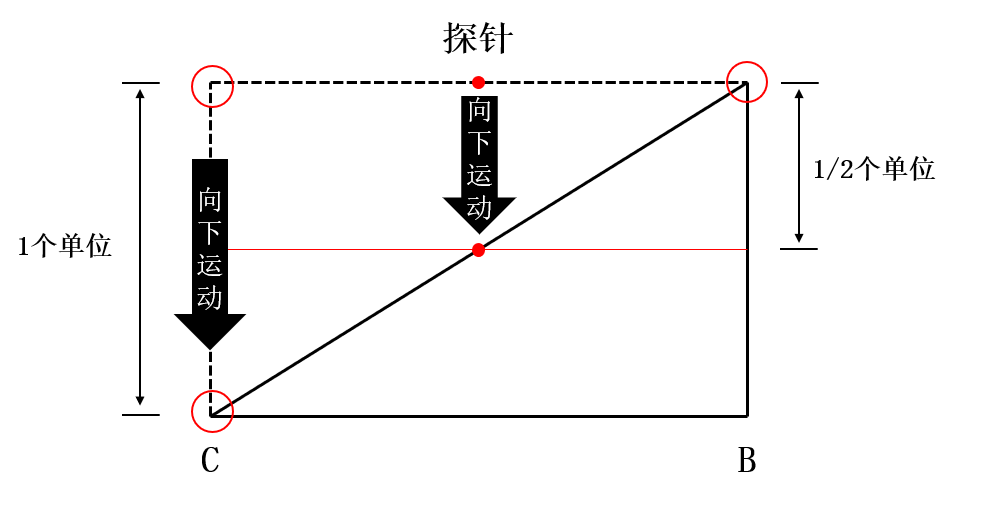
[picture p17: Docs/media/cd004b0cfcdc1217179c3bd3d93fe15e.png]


        在忽略材料加工精度与探针长度的情况下，可以近似认为通过该套机械结构的最小运动缩放比为60：1。又由于本项目使用的微分头牙距为0.5mm，步进电机最小分辨率为0.044°，故在理想情况下，可近似认为该套系统的精度为

$$
0.5mm×\frac{0.044°}{360°}×\frac{1}{60}=1.019nm
$$

## 磁吸式样品台

        样品台的结构如图所示。样品台由四个部分构成：承载PCB、钕磁铁B、钕磁铁A以及样品。承载PCB通过螺丝固定在样品台支撑板上保持固定状态，圆形钕磁铁B以锡焊的方式固定在承载PCB上，圆形钕磁铁A与圆形钕磁铁B以磁吸方式连接，圆形钕磁铁A与样品通过导电银漆连接。

        在显微镜工作时，需要提前制作以圆形钕磁铁A与样品通过导电银漆粘合而成的样品磁贴，在装载样品时仅需将样品磁贴吸附在钕磁铁B上即可。由于钕磁铁表面表现为导电性质，故可以“承载PCB-圆形钕磁铁B-圆形钕磁铁A-样品”的路径对样品施加偏置电压。本项目的磁吸式样品台可以极大程度的简化装载样品的流程。

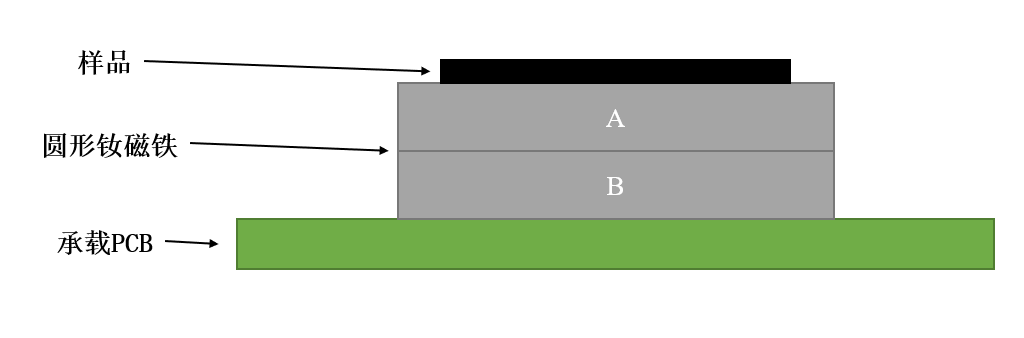
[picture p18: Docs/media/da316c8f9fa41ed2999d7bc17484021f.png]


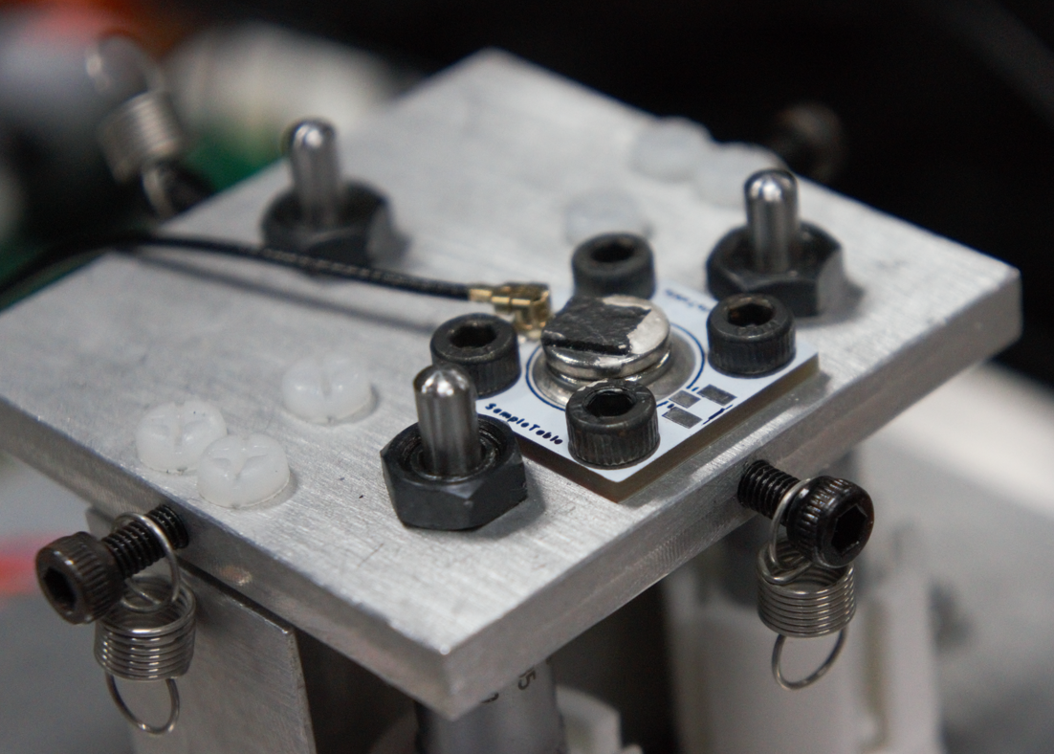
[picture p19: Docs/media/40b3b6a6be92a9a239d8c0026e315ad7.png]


## 进近算法

        本项目采用的进近算法主要由目视进近和“啄木鸟”式进近两个部分组成，步骤框图如图所示。

        在目视进近（粗进近）开始时，微分头进行调平，使活动平台水平。调平完成后，微分头A、B、C以相同的速率下降，此时活动平台水平下降。在观察到探针较为接近样品后，微分头A停止运动，微分头B、C继续下降直至在肉眼条件下观察不出探针与样品之间缝隙，此时目视进近完成。

        在“啄木鸟”式进近（细进近）阶段，该阶段的进近操作由控制系统自动完成。首先扫描头将执行Z轴伸缩，当Z轴伸缩后无法建立隧穿电流时，系统将控制微分头A下降一定高度，随后扫描头将再次进行Z轴伸缩直至隧穿电流建立为止。

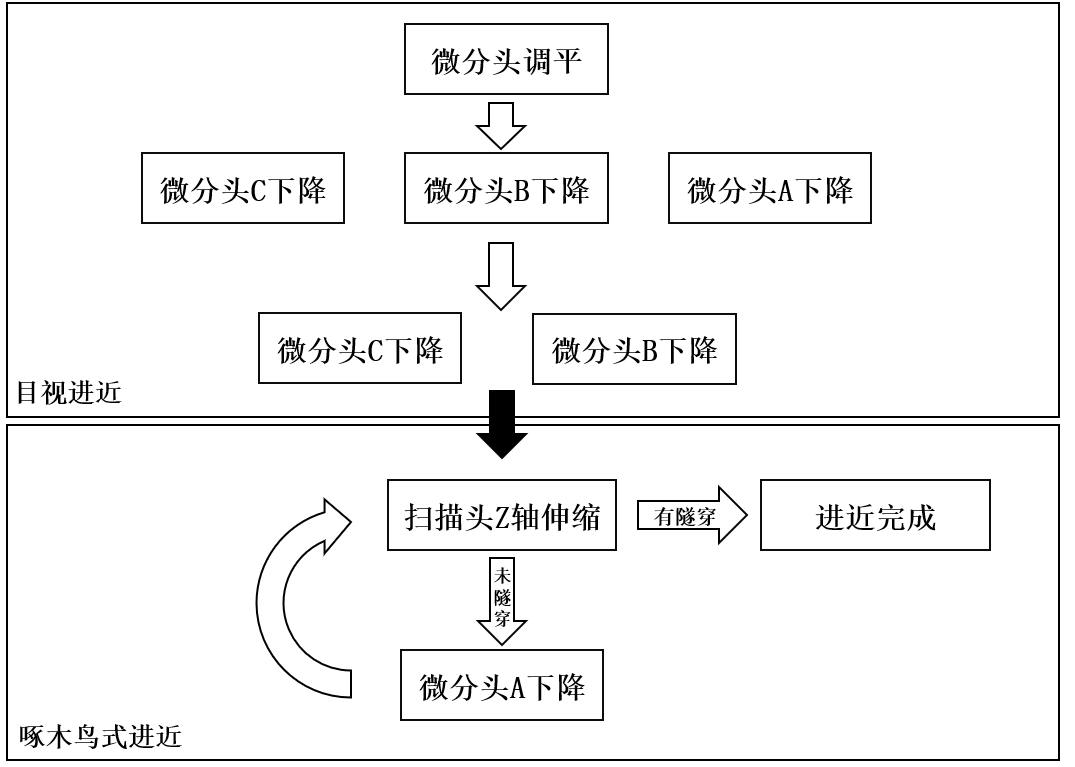
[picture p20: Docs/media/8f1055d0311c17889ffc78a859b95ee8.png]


# 参考文献

[1].    Besocke K. An easily operable scanning tunneling microscope[J]. Surface Science, 1987, 181(1-2): 145-153.

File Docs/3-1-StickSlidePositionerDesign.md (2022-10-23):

# 粘-滑压电滑台设计

		由于扫描头与支撑结构之间的热失配，导致显微镜在温度变化时，在探针与样品间将产生较大的相对位移，从而影响隧穿电流的稳定性。同时由于步进电机（热源）的存在，使得显微镜热失配问题更为严重。虽然目前的显微镜能够在预热1小时左右后达到相对稳定的热平衡，但仍有非常大的改进空间。

		热失配产生的主要原因是各个材料之间的热膨胀系数不匹配，从而导致温度变化时的膨胀程度不一致所导致的。可以通过改变进近机械结构、增设温度平衡腔体、缩小显微镜尺寸、尽量使用热膨胀系数匹配的材料等方法解决。

		特别的，对于目前的粗进近结构，由于步进电机固有的发热问题，将对显微镜整体产生较为严重的温漂。通过进一步调研后，发现一种基于粘-滑(Stick-Slip)原理的压电滑台被广泛应用于对温漂控制具有高要求的场景。可以通过自行设计一种适用于本项目的压电粘-滑滑台用于改进本项目的粗进近系统。

		如图为Hsien-Shun Liao等人设计制作的高精度、长行程压电滑台[1]，其具有结构简单、制造成本低、精度高的特点，特别适合用于本项目。

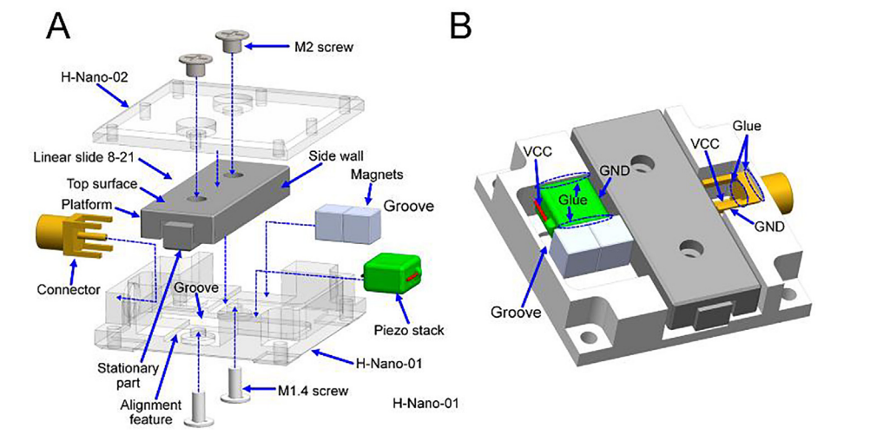
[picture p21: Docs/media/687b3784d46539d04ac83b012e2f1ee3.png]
687b3784d46539d04ac83b012e2f1ee3


# 参考文献

[1].	Liao H S, Werner C, Slipets R, et al. Low-cost, open-source XYZ nanopositioner for high-precision analytical applications[J]. HardwareX, 2022: e00317.

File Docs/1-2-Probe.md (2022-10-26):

# 扫描探针制备

        对于扫描隧道显微镜的扫描探针，最理想的情况是扫描探针的针尖仅有一个原子用于传输隧穿电流[1]。但需要制备这种探针的条件过于苛刻，且对于本项目而言难度过大。

        在参考了瑞士Nano Surf公司生产的桌面扫描隧道显微镜的操作过程以及部分爱好者在网络上公开对于扫描探针的制备方法后，采用以下方法对探针进行制备：

（1）选择导电惰性金属材料（如铂铱合金）作为探针材料，以避免制备后的针尖氧化。此处选择直径为0.3mm~0.4mm的铂金丝或钨丝作为探针材料。

（2）使用剪线钳以45°对探针丝进行剪切的同时向前拉“扯探”针丝，制备形成探针尖端。

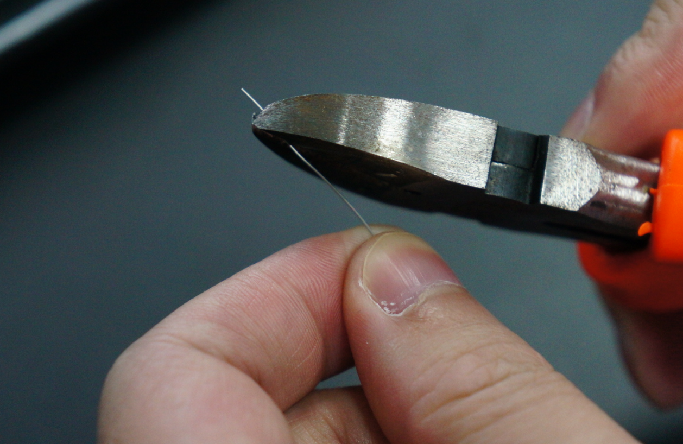
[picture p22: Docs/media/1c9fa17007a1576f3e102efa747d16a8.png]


在上述针尖制备方法的过程中，探针丝的尖端由于“拉扯”而断裂形成，断裂截面的原子分布并非绝对平整。在显微镜的实际扫描的过程中，推测隧穿电流可能由某个最为突出的原子“主导”，从而也能实现较高的分辨率。

根据普渡大学对直径为0.008"的Pt/Ir金属丝进行机械拉伸剪裁后，对针尖的SEM图像显示[2]，通过此方法制备的扫描针尖能够达到可观的尖锐程度。

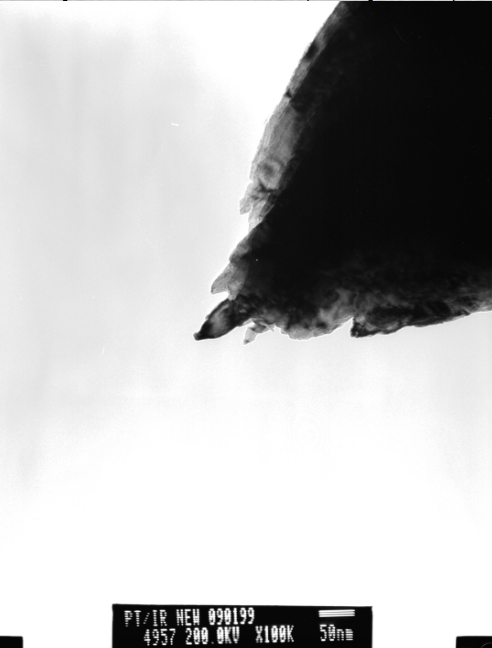
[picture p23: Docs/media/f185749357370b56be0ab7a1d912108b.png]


# 参考资料

[1].    Lounis S. Theory of scanning tunneling microscopy[J]. arXiv preprint arXiv:1404.0961, 2014.

[2].    Purdue University. TEM Pictures of STM Tips[EB/OL]. 2002[2022-9-20]. https://www.physics.purdue.edu/nanophys/uhvstm/tip.html.

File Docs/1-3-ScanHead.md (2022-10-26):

# 压电扫描头设计

## 压电扫描头器件选择

        对于扫描隧道显微镜而言，扫描头的分辨率决定了图像的分辨率。除此之外，对于隧道电流的建立也主要由扫描头来完成。考虑到空气中隧穿距离的普遍距离在10Å以内[1][2]，故需要扫描头的形变需要控制在纳米级别。

        在商业扫描隧道显微镜中，普遍采用压电晶体作为压电扫描头的执行器，但直接购买商用压电晶体管成本较高且驱动难度较大。在经过调研后发现，由John D. Alexander提出的结构[3]可以利用内置了压电晶体的压电蜂鸣器（如图）进行改造，制成能够用于扫描隧道显微镜的压电扫描头。

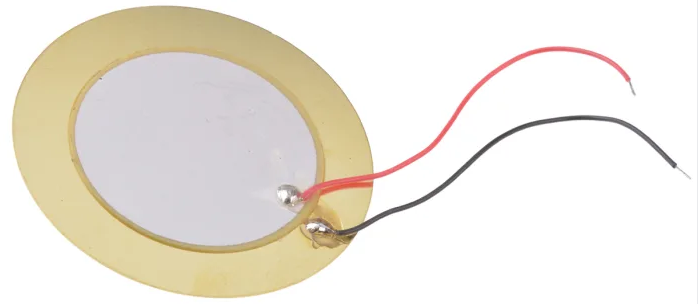
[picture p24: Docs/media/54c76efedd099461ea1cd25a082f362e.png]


## 压电蜂鸣器工作原理

常见的盘状压电蜂鸣器的侧视结构如下图所示：

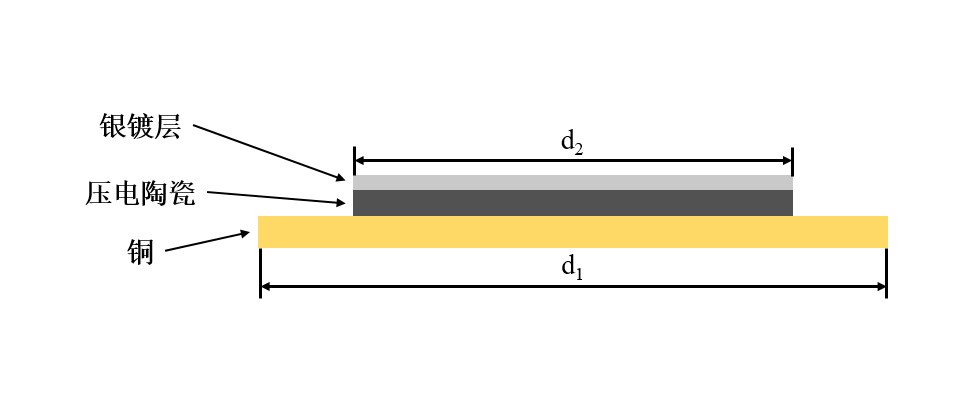
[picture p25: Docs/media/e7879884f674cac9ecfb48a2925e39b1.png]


        压电蜂鸣器主要由三个圆盘层构成：铜层、压电陶瓷层和镀银层。铜层半径为d1，压电陶瓷层及镀银层半径为d2。本项目使用的木村(muRata)7BB-20-6L0型压电蜂鸣器直径d1=20mm，d2=14mm。

        铜层与镀银层与压电陶瓷存在直接的导电接触，并且导线被分别焊接在铜层和镀银层上用于给压电陶瓷施加电场。此外，铜层除了提供导电接触外，还能够为压电蜂鸣器提供一定的机械强度以及作为蜂鸣器的振膜。

        利用逆压电效应，通过在压电陶瓷两侧施加电压，可以让压电陶瓷发生形变。对压电蜂鸣器施加不同频率的交变电压，压电蜂鸣器便会发出不同频率的声音，这即是压电蜂鸣器的工作原理。

        以7BB-20-6L0型压电蜂鸣器为例，如下图所示：当通过引线对镀银层施加正向电压时，蜂鸣器整体向镀银层方向弯曲，当对铜层施加正向电压时，蜂鸣器整体向铜层方向弯曲。

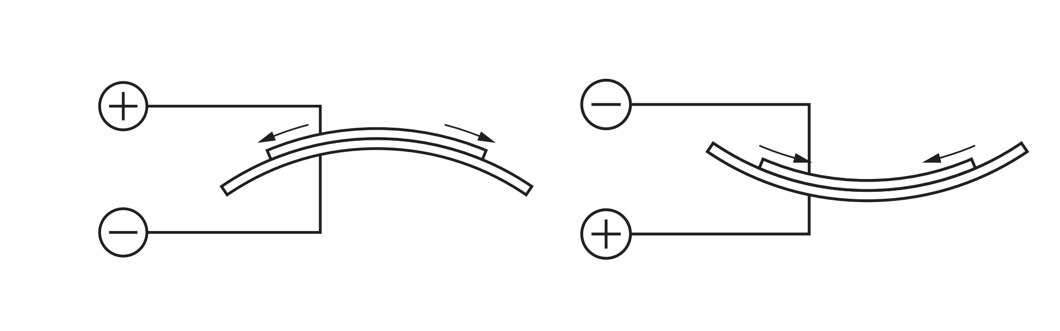
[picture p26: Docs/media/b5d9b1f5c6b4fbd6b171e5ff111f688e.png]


        对于压电陶瓷而言，存在两个需要关注的参数：即纵向压电应变常数和横向压电应变常数。纵向压电应变常数(d33)描述了电场和形变方向一致时的电场、电压对应变的转换关系，而横向压电应变常数(d31)则是描述了电场和形变方向垂直时的转换关系[4]。用公式可表达为（其中S为材料应变，d为压电常数，E为电场强度）：S=dE

        当考虑对压电陶瓷施加电压时，压电陶瓷产生的形变量可以使用以下公式表示（其中ΔL为形变量，d为压电常数，V为施加电压）：ΔL=dV

        下表列出了常用于压电蜂鸣器的压电陶瓷的横向压电应变常数：

| 压电陶瓷类型 | d31(nm/V) |
|:------:|:---------:|
| PZT-5A | -0.18     |
| BM500  | -0.16     |
| PZT-5H | -0.27     |
| BM527  | -0.25     |
| PZT-4  | -0.12     |

        对于压电蜂鸣器而言，其所能够产生的弯曲形变是利用了压电陶瓷的横向应变的特性。在图3.9中，压电蜂鸣器的圆盘形压电陶瓷在受到电场作用下沿水平方向“舒张”或“收缩”，从而产生弯曲。在应力一定的情况下，压电蜂鸣器的弯曲程度由横向应变常数和电压决定，从表3.1的参数中可以看到，常用的压电陶瓷d31在-0.12nm/V~-0.25nm/V，由此可判断将压电蜂鸣器用于扫描隧道显微镜的扫描头是可行的。

## 压电扫描头结构

        本项目的压电扫描头的实物图及结构图如图所示：

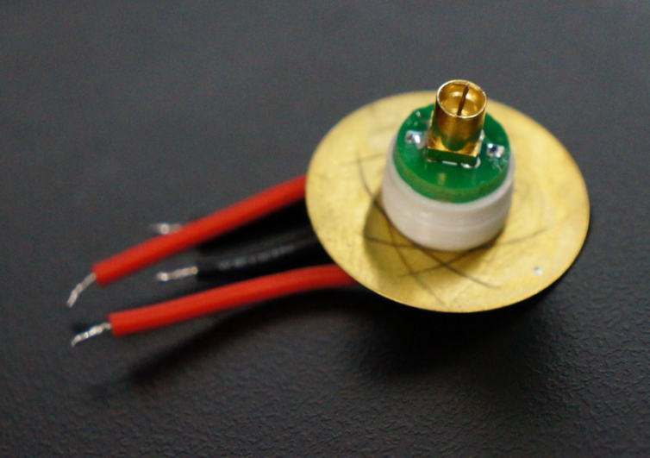
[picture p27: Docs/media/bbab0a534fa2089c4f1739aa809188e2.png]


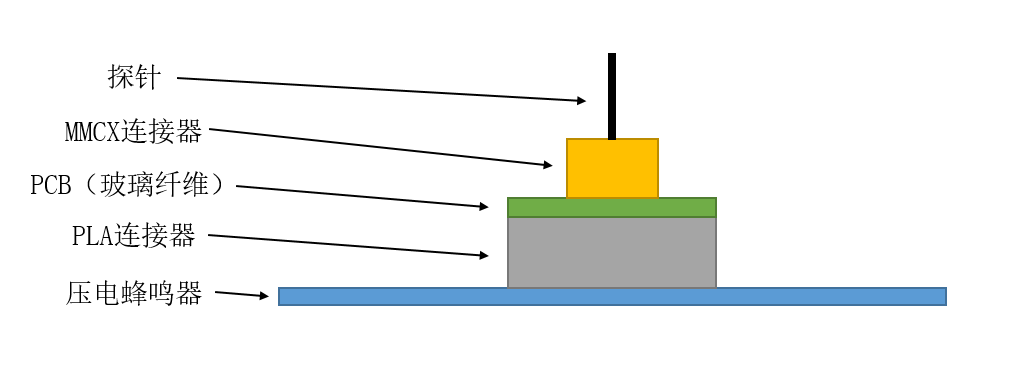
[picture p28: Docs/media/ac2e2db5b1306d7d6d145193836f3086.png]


        压电扫描头的部件由图3.11所示的五个部分组成。PLA连接器为聚乳酸的3D打印结构，用于连接压电蜂鸣器与PCB。PCB为玻璃纤维材料，为MMCX连接器提供焊盘。MMCX连接器为通讯用信号连接器，其内部具有直径为0.3~0.4mm的针座，可用于安装探针。压电蜂鸣器、PLA连接器、PCB之间使用502胶水进行粘接，PCB与MMCX连接器之间使用焊锡进行焊接固定。压电蜂鸣器的弯曲动作将通过中间的连接组件（PLA连接器、PCB、MMCX连接器）传递至探针，从而带动探针的移动。

        压电蜂鸣器的镀银层被均匀地覆盖在压电陶瓷的表面，此时的压电蜂鸣器只能实现一维弯曲。若使用切割工具将镀银层进行切割，并切割成如图所示的结构，压电蜂鸣器将能够实现三维的移动。

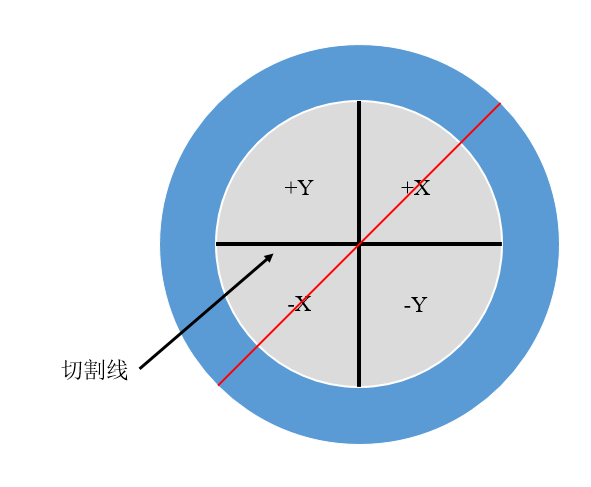
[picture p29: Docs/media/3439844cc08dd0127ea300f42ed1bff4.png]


        所示的镀银层分割为+X、-X、+Y、-Y四个区域，四个区域的镀银层互不导通。此时若让蜂鸣器的铜层接地，即电压为0，当对四个区域施加相同的正电压或负电压时，探针将被带动向上移动或向下移动。

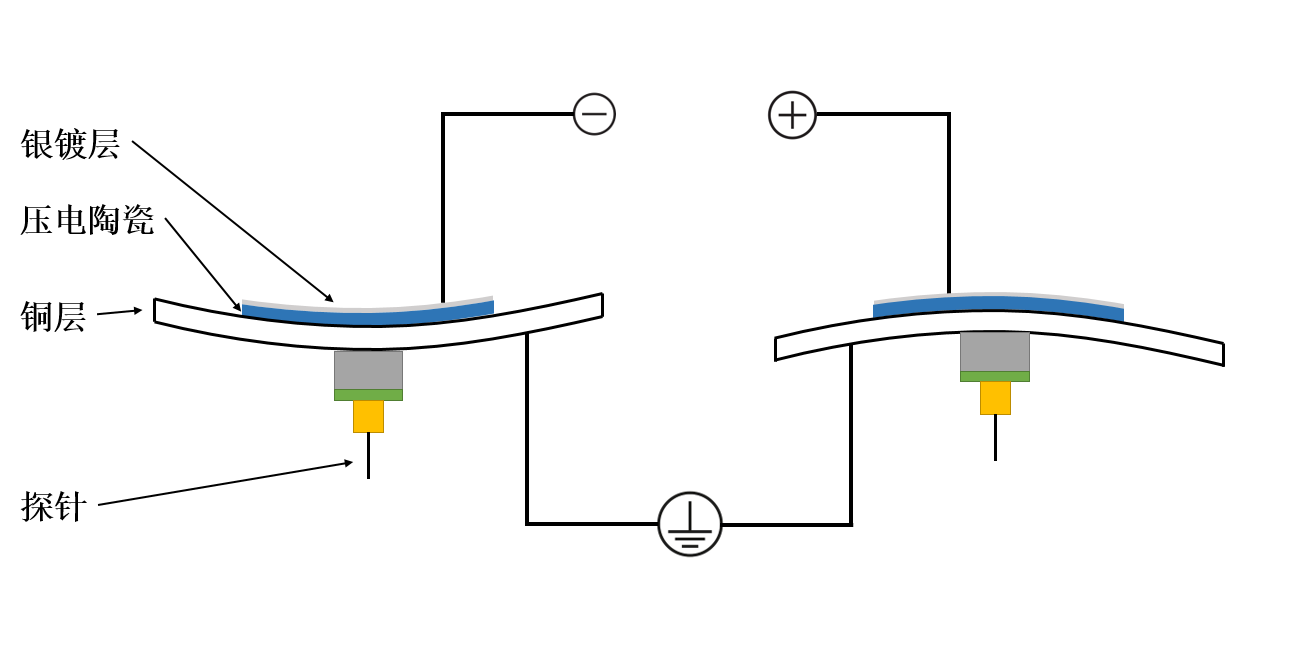
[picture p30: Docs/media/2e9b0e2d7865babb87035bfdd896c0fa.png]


        对切割图的红色线条方向进行剖视，剖视的示意图如图3.14所示。当对-X区域的镀银层施加正向电压，对+X区域的镀银层施加大小相同的反向电压时，压电陶瓷将发生“S形”弯曲，探针将被带向-X方向。反之，若对-X区域施加反向电压，对+X区域施加正向电压，探针将被带向+X方向。对于-Y、+Y区域的情况和-X、+X原理相同。

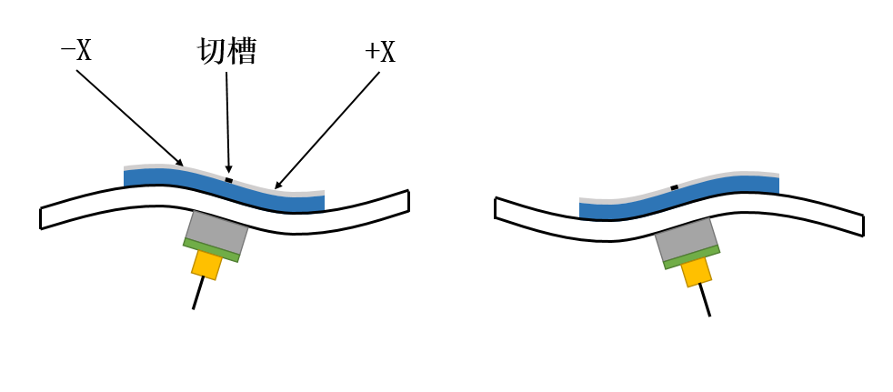
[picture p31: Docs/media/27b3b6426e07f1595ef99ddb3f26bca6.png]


        通过控制+X、-X和+Y、-Y间的相对电压差，可以实现探针的X、Y（前后左右）轴移动，通过控制四个区域整体对地（铜层）的电压差，可以实现探针的Z轴（上下）移动。

## 压电陶瓷的去极化

        目前广泛使用的压电陶瓷主要成分为锆钛酸铅Pb[Zr_x Ti_(1-x)]O_3 (0≤x≤1)，在制作过程中会将烧结好的压电陶瓷加以强场进行极化，但如果对已经极化完成的压电陶瓷施加过高的温度，压电陶瓷将去极化从而失效。

        主要成分同样为锆钛酸铅的NCE51型压电陶瓷在350~370℃将发生去极化[5]，由于muRata公司未提供7BB-20-6L0型压电蜂鸣器所用压电陶瓷的具体型号，为保险起见，在对压电蜂鸣器进行导线焊接时需要使用熔点为170℃左右的低温焊锡进行焊接，并将烙铁头温度控制在200℃左右以避免压电陶瓷发生去极化，从而影响压电扫描头的整体性能。



# 参考文献

[1].    Hahn J R, Hong Y A, Kang H. Electron tunneling across an interfacial water layer inside an STM junction: tunneling distance, barrier height and water polarization effect[J]. Applied Physics A, 1998, 66(1): S467-S472.

[2].    Woo D H, Choi E M, Yoon Y H, et al. Current–distance–voltage characteristics of electron tunneling through an electrochemical STM junction[J]. Surface science, 2007, 601(6): 1554-1559.

[3].    Alexander J D, Tortonese M, Nguyen T. Atomic force microscope with integrated optics for attachment to optical microscope: U.S. Patent 5,952,657[P]. 1999-9-14.

[4].    陈大任,李国荣,殷庆瑞.逆压电效应的压电常数和压电陶瓷微位移驱动器[J].无机材料学报,1997(06):861-866.

[5].    Fialka J, Benes P, Michlovska L, et al. Measurement of thermal depolarization effects in piezoelectric coefficients of soft PZT ceramics via the frequency and direct methods[J]. Journal of the European Ceramic Society, 2016, 36(11): 2727-2738.

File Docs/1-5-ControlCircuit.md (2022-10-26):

# 控制电路设计

## 系统结构总览



        显微镜的数字控制系统框图如图所示。在显微镜工作时，由上位机（电脑）运行的软件通过串口与主控制器进行通讯，完成对显微镜的所有控制与数据采集工作。

       主控制器负责控制三个对象：步进电机控制器、数模转换器（DAC）、模数转换器（ADC）。主控制器通过串口控制步进电机控制器完成对步进电机的驱动，通过SPI通讯协议控制数模转换器完成对扫描头的压电控制，通过SPI协议接收数模转换器采样的前级放大器数据。

## 主控制器

        由于ESP32单片机具有双核心高速处理器、多个硬件SPI接口、两个硬件串口，能够非常好地满足本项目对于主控制器的条件，故主控制器使用ESP32作为核心处理单元。主控制器与电源芯片集成在同一块控制PCB上，电源芯片为步进电机控制器以及数模、模数转换器提供电源。



        （1）交互接口方面，控制PCB上的USB接口用于与上位机进行串口通讯，为保证传输速率，波特率为250000。数模、模数转换器接口用于与数模、模数转换器的供电与数据交换，步进电机控制器接口用于与并不仅电机控制器的供电与数据交换。

        （2）电源设计方面，控制PCB一共设计了两组电源：用于模拟电路用途的电源以及用于数字用途的电源，两组电源由分立的锂电池进行供电，并且两组电源电路的大地进行了隔离以减少噪音耦合。

        对于数字用途的电源，其包括5V和3.3V两个电源平面，5V电源平面由普通的开关升压芯片将锂电池3.7V电压升压至5V，用于对步进电机驱动器的供电。3.3V电源平面由低压差线性稳压器（LDO）将锂电池电压降压至3.3V，用于ESP32单片机的供电。

        对于模拟用途的电源，其包括5V、±12V、±15V五个低噪声电源平面，这里的5V平面与数字用途的5V平面无连接关系。模拟通途的电源平面由四组2S（即两个3.7V锂电池包串联）提供电压，经过低噪声LDO降压至各个电压的电源平面。正电源使用的LDO型号为ADP7142，其最低噪声为11μVrms。负电源使用的LDO型号为ADP7182，其最低噪声为18μVrms。5V电源平面用于对ADC的供电，±15V电源平面用于DAC的供电，±12V电源平面用于前级放大器的供电。由于DAC、ADC以及前级放大器对电源噪声由较高的要求，故再次采用了低噪声LDO进行供电。





        （3）单片机逻辑设计方面，由于ESP32具有两个独立的CPU核心，故在程序设计时可以设计两个循环在两个核心上分别同时运行，用于接收上位机命令与执行进近、扫描等操作。



## 步进电机控制器

        本项目采用了自主设计的步进电机驱动器对步进电机进行驱动，下图为驱动器的原理图。

        步进电机驱动器采用ATMEGA328P单片机作为主控，ULN2003大电流驱动阵列作为线圈通断控制器。ATMEGA328P能够接受来自主控制器的串口型号，从而实现对步进电机状态的精确控制。





## 数模、模数转换器

        数模转换器（DAC）即是能够将数字信号转换为模拟电压的一种器件，通过DAC能够使得上位机以及主控制器的信号转换为模拟电压传递给扫描头，从而实现扫描头控制。

        对于扫描头中的压电陶瓷而言，对其施加的电压大小决定了压电陶瓷形变量大小，即扫描图的运动范围大小，故DAC的分辨率将直接决定了扫描头的分辨率。在综合了性能与价格考虑后，本项目采用了AD5761型16位分辨率DAC，该芯片能够输出±10V范围的电压。本项目使用了四颗AD5761芯片，其中三颗用于控制压电扫描头，一颗用于对样品施加偏置电压。



        模数转换器（ADC）的功能与DAC相反，其是能够读取模拟电压并将模拟电压值转换成数字量的一种器件。本项目采用ADS8689型16为分辨率ADC，用于读取前级放大器的输出电压。该芯片能够读取±12.288V范围的电压，能够非常好的适配前级放大器的输出范围，并且提供100kSPS的采样速率，能够在扫描隧道显微镜成像时提供较高的扫描速度。

        对于DAC/ADC，其能够输出/读取电压模拟量的最小电压间隔可通过下式计算：

$$
\Delta V=\frac{输入/输出电压范围}{2^{分辨率}}
$$

        通过公式，可计算出AD5761型DAC工作在±10V范围时的能够输出的最小电压间隔为：

$$
\Delta V1=\frac{20}{2^{16}}=0.31mV
$$

     DS8689工作在±12.288V范围时能够读取的最小电压间隔范围为：

$$
\Delta V2=\frac{24.456}{2^{16}}=0.37mV
$$

## 压电扫描头的电压运算器

        在压电扫描头原理介绍中，压电蜂鸣器被分割为四个区域，通过对四个施加不同电压能够实现扫描头的三维运动。在实际操作中，压电蜂鸣器的铜层接地，保持零电位，控制过程中只需要对被分割的四个区域施加电压即可。

        同样提到，对四个区域施加相同的正向或反向电压时，压电扫描头将向在Z轴运动，在+X、-X区域或+Y、-Y区域施加方向相反且大小相等的电压时，压电扫描头将可以实现X、Y轴运动。

        故在实际操作中，仅需要DAC提供三组电压X、Y、Z，并通过运算放大器组成的压电扫描头电压运算器将X、Y、Z电压运算为四组大小为Z+Y、Z-Y、Z+X、Z-X的电压即可完成三维电压对压电扫描头四个区域电压的解算。



        通过上图所示的四颗运算放大器组成的加减法运算器即可完成对电压的转换。U9.1将DAC输出的电压Z与电压X进行加法运算，输出Z+X电压，U9.2将DAC输出的电压Z与电压X进行减法运算，输出Z-X电压，U10.1、U10.2同理。



## 上位机设计

        上位机控制系统主要由两部分组成：显微镜控制单元以及成像单元。显微镜控制单元通过串口命令控制主控制器，实现目视进近、“啄木鸟”式进近以及曲线测量、图像扫描的功能，成像单元则负责将扫描数据转换为通用图像。显微镜控制单元以及成像单元的程序均使用Python进行编写，QT进行界面设计。

        下面是显微镜控制单元的用户交互界面（GUI）组成：





        显微镜控制单元的界面由两部分组成：串口连接控制面板（UART Port Select）以及显微镜行为控制面板。串口连接控制面板位于GUI的最底端，提供了串口扫描、串口选择、波特率选择及连接的功能。在串口未连接成功时，显微镜行为控制面板将不可用。

        显微镜行为控制面板共有三个选项卡，包括粗进近控制（Coarse Approach）、细进近控制及扫描（Fine Approach/SCAN）以及手动调试（Manual Control）。
在粗进近控制选项卡中，能够对步进电机进行控制，实现目视进近。在细进近及扫描选项卡中，能够对样品偏置电压、进近速度、扫描速度等参数进行设定，实现“啄木鸟”式进近控制以及图像扫描功能。

        下面是成像单元的GUI组成：



        成像单元能够读取显微镜控制单元输出的扫描原始数据并将其转换为通用的图像格式。

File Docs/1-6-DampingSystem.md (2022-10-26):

# 隔震系统搭建

        由于缺少微小震动评估设备，故本项目在结合现有的扫描隧道显微镜的减震指导理论以及搭建成本及难度后对本项目的减震系统进行简单构建。

        对于高频震动的隔离，一种以金属片-氟橡胶交替的堆叠系统被提出用于扫描隧道显微镜的震动隔离[1]，再通过搭配与堆叠减震系统谐振频率不同的另一级减震系统能够实现较好效果的减震[2]。本项目使用悬挂系统进行一级减震，金属片-氟橡胶交替的堆叠系统进行二级减震。





# 参考文献

[1].    Oliva A I, Aguilar M, Sosa V. Low-and high-frequency vibration isolation for scanning probe microscopy[J]. Measurement Science and Technology, 1998, 9(3): 383.

[2].    Okano M, Kajimura K, Wakiyama S, et al. Vibration isolation for scanning tunneling microscopy[J]. Journal of Vacuum Science & Technology A: Vacuum, Surfaces, and Films, 1987, 5(6): 3313-3320.

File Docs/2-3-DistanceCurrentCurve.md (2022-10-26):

# 距离-隧穿电流测试

plot7

plot8

        上图为对热解石墨（HOPG）样品在偏置电压为50mV下的隧穿距离-电流测试曲线。压电扫描头的Z轴步长电压为310μV，步长变化、采样时间间隔为1ms。从图中可以看出，该曲线特性满足指数特征，说明了压电扫描头的Z轴方向进给均匀，且装置所捕获的信号为隧穿电流信号。

plot9

        上图为对热解石墨（HOPG）样品在偏置电压为50mV，步长变化、采样间隔为1ms下不同Z轴步长电压下的隧穿距离-电流测试曲线。其中，1S对应位为310μV的步长，5S对应为5×310μV=1.55mV的步长。从图中可以看出，在不同的Z轴运动速率下，曲线仍表现出指数增长的特性。

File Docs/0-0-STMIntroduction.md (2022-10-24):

# STM简介

        扫描隧道显微镜（STM）是基于量子隧穿效应，利用隧穿电流特性工作的一种能够实现原子级分辨率成像的显微镜。

        通过将导电探针悬停在通电样品表面几纳米处进行栅格扫描，监测隧穿电流变化情况，扫描隧道显微镜能够实现样品表面形貌成像[1]。由于隧穿电流随距离指数性变化的特征，扫描隧道显微镜能够达到0.1nm的横向分辨率与0.01nm的垂直分辨率[2]。

# 量子隧穿效应

***推导仅供参考，若有错误，欢迎指正。**

***不想看推导部分的可直接看最后的结论。**

        在经典力学中，在一维情况下，总能量为E的电子在位置为x处的运动情况可以用以下公式表示：

$$
E=\frac{1}{2} m v^2+V(x)
$$

        其中，m为电子质量，v为电子速度，V(x)为与电子位置x处有关的势能。由式子(2.1)可知，只有当E>Ep时，电子才具有正值的速度。因此，若某一位置势能Ep1>E时，电子将不可能到达该位置。

        德布罗意在1924年提出电子如光的波粒二象性一样，具有波的性质，并且电子的波长λ可以通过公式(2.2)描述：

$$
E=\frac{h}{p}
$$

其中，h为普朗克常量，p为电子动量。

        可以将扫描隧道显微镜的势能模型简化为下图所示的一维形式，探针与样品间的间隙被描述为方势垒，其中红色横线为电子能量：



即势能可以通过公式描述为：V(x)=0(x<a, x>a), V(x)=V_1(a<x<b)

        在量子力学中，电子将被满足薛定谔方程的波函数ψ(x)描述。此处讨论电子在一维定态下量子隧穿的情况，设电子的势能方程为：

$$
V=V(x)
$$

此时波函数也只和空间坐标有关：

$$
\psi=\psi(x)
$$

在定态情况下，不含时薛定谔方程取这样的形式：

$$
\frac{d^2 \psi}{d x^2}+\frac{2 m}{\hbar^2}(E-V) \psi=0
$$

其中：

$$
ℏ=\frac{h}{2π}
$$

        在扫描隧道显微镜工作时，电子可视为从探针区域射向势垒，但由于电子能量小于势垒，在经典力学角度上电子不可能跨过势垒到达样品处，即在样品与探针间不可能存在电流。

        从经典力学角度对电子存在性上进行分析，可将空间区域分为经典允许区与经典禁区。当电子位于探针区域时，此时的电子总能量大于所处位置势能E>V，从经典力学的角度上看，电子能够位于该区域，即经典允许区。当电子处于真空区域时，电子的总能量小于所处位置势能E<V，从经典力学的角度上看电子不可能运动到该区域，即经典禁区。

        在经典允许区中，V=0，薛定谔方程表示为：

$$
\psi^{\prime \prime}+\frac{2 m E}{\hbar^2} \psi=0
$$

设：

$$
\frac{2 m E}{\hbar^2}=k^2
$$

则方程变为：

$$
\psi^{\prime \prime}+k^2 \psi=0
$$

该微分方程的通解为：

$$
\psi_1(x)=A \sin (k x+\delta), \delta<\pi
$$

在经典禁区中的薛定谔方程为：

$$
\psi^{\prime \prime}-\frac{2 m}{\hbar^2}(V-E) \psi=0
$$

设：

$$
\frac{2 m}{\hbar^2}(V-E)=\beta^2
$$

因为E<V1，所以β为实数。此时经典禁区的薛定谔方程变为：

$$
\psi^{\prime \prime}+k^2 \psi=0
$$

该方程的形式解为：

$$
\psi \sim e^{\pm \beta x}
$$

        可见，在经典力学中不可能出现电子的真空势垒中，在量子力学中仍然存在概率分布，并且其以指数形式衰减。

        即对于如势垒模型图描述的模型中，电子将有概率穿过真空势垒，并在样品区域产生透射波。这种电子能够穿透比其能量更高的势垒的效应即量子隧穿效应。

        通过对该模型的边界条件以及连续条件可求解[3][4][5]得到隧穿电流与真空势垒的关系为：

$$
I \propto e^{-2 \kappa d}
$$

 其中：

$$
\kappa=\frac{\sqrt{2m(V-E)}}{\hbar}
$$

        d为探针样品间距。从公式可以看出，当进入隧穿距离后，探针与样品间距与隧穿电流呈指数关系。当探针样品间距离变化0.1nm左右时，隧穿电流大小将改变一个量级[6]，这也为扫描隧道显微镜的超高分辨率提供了理论基础。

# 参考文献

[1].    Lounis S. Theory of scanning tunneling microscopy[J]. arXiv preprint arXiv:1404.0961, 2014.

[2].    Bai C. Scanning tunneling microscopy and its application[M]. Springer Science & Business Media, 2000.

[3].    Baird D, Shew A. Probing the history of scanning tunneling microscopy[J]. Discovering the nanoscale, 2004, 2: 145-156.

[4].    Merzbacher E. Quantum mechanics[M]. Jones & Bartlett Publishers, 1961.

[5].    曾谨言. 量子力学导论[M]. 第二版. 北京大学出版社, 2001.

[6].    王琦. 高稳定扫描隧道显微镜的研制与应用[D].  中国科学技术大学,2014.

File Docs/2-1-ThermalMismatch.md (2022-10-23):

# 热失配估算

## 估算

        对于纳米尺度的隧穿距离而言，温度引起的材料膨胀将变得难以忽视。由于探针各部分材料与支撑结构材料的热膨胀系数不一致，在显微镜温度发生变化时，探针将与样品间发生相对位移。

        下面将对扫描头与支撑结构间发生的膨胀热失配进行简单的评估。



        支撑结构部分由轴承钢、铝材料组成，扫描头由聚乳酸、玻璃纤维（玻璃增强环氧树脂）、探针（铂）组成。下表列出了这些材料的线性热膨胀系数（常温）[1][2][3]。



    将支撑结构部分各材料的热膨胀系数以及扫描头部分各材料的热膨胀系数对长度加权后再进行差值运算，将可以对热失配进行简单估算：

$$
drift=L_{Al}\alpha_{Al}+L_{St} \alpha_{St}-L_{PLA} \alpha_{PLA}-L_{GRE}\alpha_{GRE}-L_{Cu} \alpha_{Cu}-L_{pt} α_{pt}
$$

取L_Al=8，L_St=4.6，α_St=10.5，L_PLA=5，L_GRE=1.6，L_Cu=0.5，L_pt=5.5，带入式计算可得热失配为-252.24 nm·℃^(-1)，即若显微镜整体结构温度上升1℃，探针将会相对支撑结构下降252.24nm。

## 现象验证

        在显微镜启动阶段时，探针通过进近算法进入隧穿距离后，在未干预探针动作的情况下隧穿电流呈现上升趋。而在显微镜启动一小时左右后，探针进入隧穿距离能够对隧穿电流进行保持，并且在增强系统散热后，在未干预探针动作的情况下隧穿电流呈下降趋势。

        分析上述现象出现的原因是由于步进电机存在发热，在显微镜启动阶段整体热量未平衡，热量上升将导致探针位置下降，隧穿距离减小，从而导致隧穿电流增加。而在显微镜启动一小时左右后，显微镜整体热量耗散平衡，显微镜整体温度基本保持不变，此时能够保持隧穿距离。在增强系统散热后，由于整体温度的下降将导致探针上升，隧穿距离增大，从而导致隧穿电流减少。

# 参考文献

[1].    Instrumentation reference book[M]. Butterworth-Heinemann, 2009.

[2].    Lanza di Scalea F. Measurement of thermal expansion coefficients of composites using strain gages[J]. Experimental mechanics, 1998, 38(4): 233-241.

[3].    Wijnen B, Sanders P, Pearce J M. Improved model and experimental validation of deformation in fused filament fabrication of polylactic acid[J]. Progress in Additive Manufacturing, 2018, 3(4): 193-203.

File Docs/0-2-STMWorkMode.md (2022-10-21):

# 扫描隧道显微镜工作模式

## 恒高扫描模式

        在恒高扫描模式中，扫描头的Z轴的高度将固定，通过控制X、Y轴的移动完成对样品表面的扫描，其扫描路径如图所示。在该模式下，样品的形貌变化通过隧穿电流变化体现，当隧穿电流变大时，表示样品表面存在突起，当隧穿电流减小时，表示样品表面存在凹陷。但由于样品表面的平整性不能完全保证，若样品表面某处存在大于探针悬停距离（隧穿距离）的突起时，探针在扫描该处时将与突起碰撞，从而导致探针针尖损毁。



## 恒流扫描模式

        在恒流扫描模式中，扫描头在对X、Y轴扫描的过程中，将控制探针Z轴的高度使隧穿电流大小恒定，即在扫描过程中探针与样品间距离保持恒定，Z轴运动轨迹呈现为贴合样品形貌起伏进行扫描，如图所示。扫描路径在扫描完成后通过分析Z轴位置信息将可以得出样品表面的形貌状态。在扫描隧道显微镜扫描的过程中通常会选择恒流扫描模式，以避免针尖损毁的情况发生。



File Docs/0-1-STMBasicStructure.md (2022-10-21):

# STM基本结构

## 整体结构



        扫描隧道显微镜的整体结构如图所示，其主要部件包括：机械进近结构、扫描头、探针、样品、前级放大器、控制及采集电路、控制及成像系统、隔音/隔震系统。

## 机械进近结构

        机械进近结构负责将探针与样品进近到隧穿距离内，通常这个距离在1纳米左右。为了实现如此小尺度的进近，比较广泛的解决方案是利用机械结构设计进行位移的比例缩放[1]，通过将较大的位移缩放为小尺度的位移，从而实现精细移动。

        对于机械结构的控制，通常会引入步进电机作为位移驱动器。但是步进电机的使用会额外引入热噪声，为了避免热漂移问题，目前最合适作为STM的位移驱动器马达是粘-滑压电马达。

## 扫描头

        在机械进近结构将探针进近到隧穿距离后，扫描头将负责控制探针进行X、Y、Z轴移动，对样品表面进行扫描，并且扫描头的位移精度决定了最终成像的图像精度。为了实现微小位移，目前，以锆钛酸铅为主要成分的压电陶瓷（PZT）被广泛被应用与扫描隧道显微镜的扫描头中。由于逆压电效应，通过对压电陶瓷施加电压，压电陶瓷产生的位移将可以带动探针实现纳米级的X、Y、Z轴移动。

## 探针

        对于扫描隧道显微镜而言，隧穿电流最好由探针针尖的单个原子进行拾取，故需要原子级尖锐的针尖。对于针尖的制备，通常会选择金、铂等不易氧化的惰性材料进行电解制备而成[2]。但根据Nano Surf公司生产的STM技术资料以及普渡大学的资料显示，使用剪线钳对金属丝进行拉伸式剪切所得到的探针同样能够实现原子级分辨率。

## 前级放大器

        由于隧穿电流通常在纳安数量级，故需要前级放大器对该数量级下的隧穿电流进行信号放大处理。在扫描隧道显微镜中，通常采用基于运算放大器的跨阻放大器[3]将隧穿电流信号转换为数字信号。

## 控制及采集电路

        控制及采集电路主要负责控制机械进近结构进行进近、控制扫描头进行图像扫描以及采集前级放大器放大后的隧穿电流信号。通常控制及采集电路需要包括数模、模数转换器以及电机控制器。

## 控制及成像系统

        控制及成像系统通常为运行在计算机上的能够与用于进行交互的程序。用户通过程序向控制电路发送信号，完成对样品的图像扫描头，通过程序内部的图像转换程序实现隧穿电流对可视化图像的转换。

## 隔音、隔震系统

        由于扫描隧道显微镜的成像尺度在原子级，故对机械震动以及声波震动的敏感性极高，故需要搭建隔音、隔震系统保证扫描隧道显微镜工作在最佳环境。

# 参考文献

[1].    Grafstrom S, Kowalski J, Neumann R. Design and detailed analysis of a scanning tunnelling microscope[J]. Measurement Science and Technology, 1990, 1(2): 139.

[2].    Nam A J, Teren A, Lusby T A, et al. Benign making of sharp tips for STM and FIM: Pt, Ir, Au, Pd, and Rh[J]. Journal of Vacuum Science & Technology B: Microelectronics 

[3].    Petersen J P, Kandel S A. Circuit design considerations for current preamplifiers for scanning tunneling microscopy[J]. 2017.

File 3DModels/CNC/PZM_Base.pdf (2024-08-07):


M5






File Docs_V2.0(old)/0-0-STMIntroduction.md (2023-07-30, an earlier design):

# STM简介

        扫描隧道显微镜（STM）是基于量子隧穿效应，利用隧穿电流特性工作的一种能够实现原子级分辨率成像的显微镜。

        通过将导电探针悬停在通电样品表面几纳米处进行栅格扫描，监测隧穿电流变化情况，扫描隧道显微镜能够实现样品表面形貌成像[1]。由于隧穿电流随距离指数性变化的特征，扫描隧道显微镜能够达到0.1nm的横向分辨率与0.01nm的垂直分辨率[2]。

# 量子隧穿效应

***推导仅供参考，若有错误，欢迎指正。**

***不想看推导部分的可直接看最后的结论。**

        在经典力学中，在一维情况下，总能量为E的电子在位置为x处的运动情况可以用以下公式表示：

$$
E=\frac{1}{2} m v^2+V(x)
$$

        其中，m为电子质量，v为电子速度，V(x)为与电子位置x处有关的势能。由式子(2.1)可知，只有当E>Ep时，电子才具有正值的速度。因此，若某一位置势能Ep1>E时，电子将不可能到达该位置。

        德布罗意在1924年提出电子如光的波粒二象性一样，具有波的性质，并且电子的波长λ可以通过公式(2.2)描述：

$$
E=\frac{h}{p}
$$

其中，h为普朗克常量，p为电子动量。

        可以将扫描隧道显微镜的势能模型简化为下图所示的一维形式，探针与样品间的间隙被描述为方势垒，其中红色横线为电子能量：



即势能可以通过公式描述为：V(x)=0(x<a, x>a), V(x)=V_1(a<x<b)

        在量子力学中，电子将被满足薛定谔方程的波函数ψ(x)描述。此处讨论电子在一维定态下量子隧穿的情况，设电子的势能方程为：

$$
V=V(x)
$$

此时波函数也只和空间坐标有关：

$$
\psi=\psi(x)
$$

在定态情况下，不含时薛定谔方程取这样的形式：

$$
\frac{d^2 \psi}{d x^2}+\frac{\hbar^2}{2 m}(E-V) \psi=0
$$

其中：

$$
ℏ=\frac{h}{2π}
$$

        在扫描隧道显微镜工作时，电子可视为从探针区域射向势垒，但由于电子能量小于势垒，在经典力学角度上电子不可能跨过势垒到达样品处，即在样品与探针间不可能存在电流。

        从经典力学角度对电子存在性上进行分析，可将空间区域分为经典允许区与经典禁区。当电子位于探针区域时，此时的电子总能量大于所处位置势能E>V，从经典力学的角度上看，电子能够位于该区域，即经典允许区。当电子处于真空区域时，电子的总能量小于所处位置势能E<V，从经典力学的角度上看电子不可能运动到该区域，即经典禁区。

        在经典允许区中，V=0，薛定谔方程表示为：

$$
\psi^{\prime \prime}+\frac{2 m E}{\hbar^2} \psi=0
$$

设：

$$
\frac{2 m E}{\hbar^2}=k^2
$$

则方程变为：

$$
\psi^{\prime \prime}+k^2 \psi=0
$$

该微分方程的通解为：

$$
\psi_1(x)=A \sin (k x+\delta), \delta<\pi
$$

在经典禁区中的薛定谔方程为：

$$
\psi^{\prime \prime}-\frac{2 m}{\hbar^2}(V-E) \psi=0
$$

设：

$$
\frac{2 m}{\hbar^2}(V-E)=\beta^2
$$

因为E<V1，所以β为实数。此时经典禁区的薛定谔方程变为：

$$
\psi^{\prime \prime}+k^2 \psi=0
$$

该方程的形式解为：

$$
\psi \sim e^{\pm \beta x}
$$

        可见，在经典力学中不可能出现电子的真空势垒中，在量子力学中仍然存在概率分布，并且其以指数形式衰减。

        即对于如势垒模型图描述的模型中，电子将有概率穿过真空势垒，并在样品区域产生透射波。这种电子能够穿透比其能量更高的势垒的效应即量子隧穿效应。

        通过对该模型的边界条件以及连续条件可求解[3][4][5]得到隧穿电流与真空势垒的关系为：

$$
I \propto e^{-2 \kappa d}
$$

 其中：

$$
\kappa=\frac{\sqrt{2m(V-E)}}{\hbar}
$$

        d为探针样品间距。从公式可以看出，当进入隧穿距离后，探针与样品间距与隧穿电流呈指数关系。当探针样品间距离变化0.1nm左右时，隧穿电流大小将改变一个量级[6]，这也为扫描隧道显微镜的超高分辨率提供了理论基础。

# 参考文献

[1].    Lounis S. Theory of scanning tunneling microscopy[J]. arXiv preprint arXiv:1404.0961, 2014.

[2].    Bai C. Scanning tunneling microscopy and its application[M]. Springer Science & Business Media, 2000.

[3].    Baird D, Shew A. Probing the history of scanning tunneling microscopy[J]. Discovering the nanoscale, 2004, 2: 145-156.

[4].    Merzbacher E. Quantum mechanics[M]. Jones & Bartlett Publishers, 1961.

[5].    曾谨言. 量子力学导论[M]. 第二版. 北京大学出版社, 2001.

[6].    王琦. 高稳定扫描隧道显微镜的研制与应用[D].  中国科学技术大学,2014.

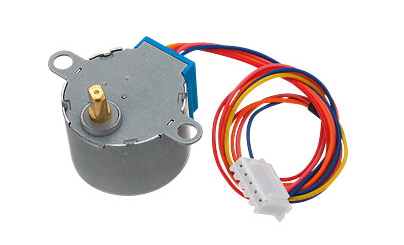
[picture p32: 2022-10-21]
Docs/media/407f72721121ac9294ce46234ebbd82b.png

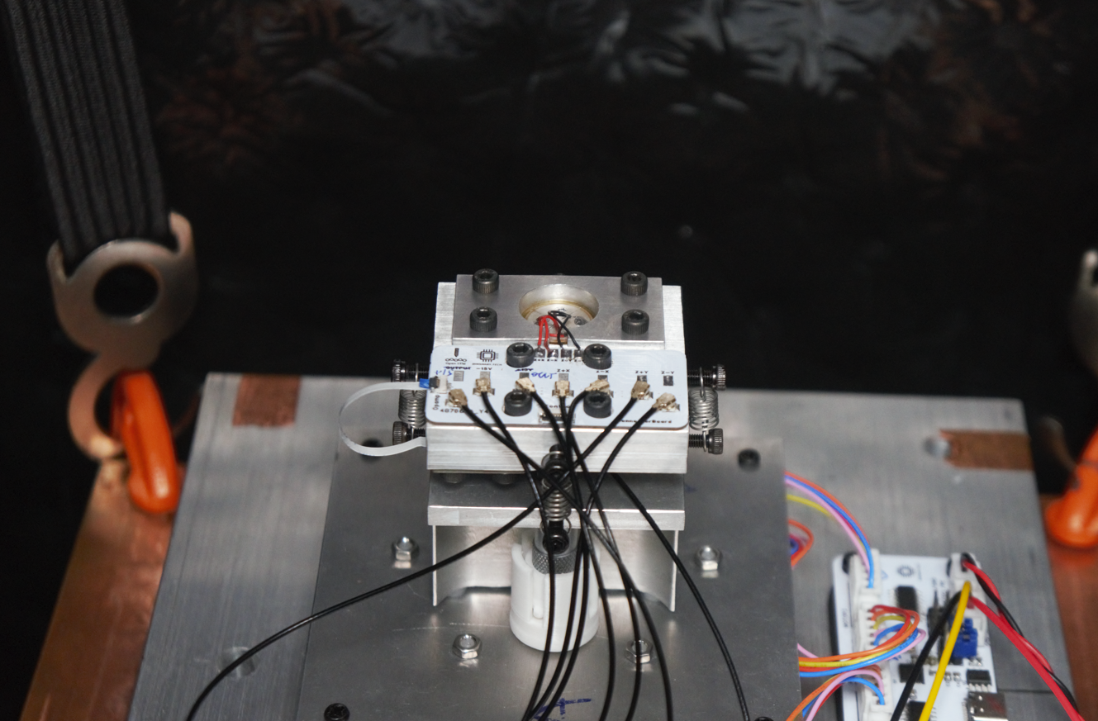
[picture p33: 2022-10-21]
Docs/media/a59f6eef87339732a125d78b0beff01f.png

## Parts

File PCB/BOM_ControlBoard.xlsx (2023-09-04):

Designator | Component | Number | Cost per unit -CNY | Total cost -CNY | Source of materials | Material type | Package | Value
C1,C3,C5,C7,C9,C11,C13,C15,C17,C19,C21,C23,C26,C27,C29,C30,C32,C33,C35,C36,C43,C44,C45,C46,C57,C59,C65,C67,C70,C74,C76,C78,C79 | CL10B104KA8NNNC | 33 | 0.018 | 0.59 | LCSC (https://www.szlcsc.com/) | Capacitor | C0603 | 100nF
C2,C4,C6,C8,C10,C12,C14,C16,C18,C20,C22,C24,C25,C28,C31,C34,C47,C58,C60,C66,C68,C72,C73,C75,C77 | GRM188R61E106MA73D | 25 | 0.16 | 4 | LCSC (https://www.szlcsc.com/) | Capacitor | C0603 | 10uF
C37,C38,C39,C40,C41,C42 | 0603B472K500NT | 6 | 0.02 | 0.12 | LCSC | Capacitor | C0603 | 4.7nF
C48 | CL10A226MP8NUNE | 1 | 0.08 | 0.08 | LCSC | Capacitor | C0603 | 22uF
C49,C51,C52 | CL10A105KA8NNNC | 3 | 0.03 | 0.09 | LCSC | Capacitor | C0603 | 1uF
C53 | CL10C331JB8NNNC | 1 | 0.05 | 0.05 | LCSC | Capacitor | C0603 | 330pF
CN1 | X9555WR-2x07-6TV01 | 1 | 1 | 1 | LCSC | Connecor | CONN-TH_14P-P2.54_XKB_X9555WR-2X7-6TV01
H1,H2,H3 | PZ254V-11-02P | 3 | 0.09 | 0.27 | LCSC | Connecor | HDR-TH_2P-P2.54-V-F
LED1,LED2,LED3,LED4,LED5,LED6,LED7,LED8 | 19-217/R6C-AL1M2VY/3T | 8 | 0.1 | 0.8 | LCSC | LED | LED0603-R-RD
R1,R2,R3,R27,R37 | 0603WAF1001T5E | 5 | 0.0035 | 0.0175 | LCSC | Resistor | R0603 | 1kΩ
R5,R7,R8,R10,R11,R12,R13,R15,R16,R17,R18,R20,R21,R22 | ARG03DTC3001 | 14 | 0.05 | 0.7 | LCSC | Resistor | R0603 | 3k
R6,R9,R14,R19,R30,R31 | 0603WAF2200T5E | 6 | 0.006 | 0.036 | LCSC | Resistor | R0603 | 220Ω
R23,R26 | RL0603FR-070R47L | 2 | 0.1 | 0.2 | LCSC | Resistor | R0603 | 0.47Ω
R24,R25 | 0603WAF1002T5E | 2 | 0.005 | 0.01 | LCSC | Resistor | R0603 | 10k
R33 | 0603WAF4701T5E | 1 | 0.007 | 0.007 | LCSC | Resistor | R0603 | 4.7kΩ
R35,R36 | 0603WAF1002T5E | 2 | 0.005 | 0.01 | LCSC | Resistor | R0603 | 10kΩ
RF1,RF2,RF3,RF4,RF5,RF6,RF7,RF8,RF9,RF10 | KH-SMA-KE-Z | 10 | 1.91 | 19.1 | LCSC | Connector | SMA-TH_KH-SMA-KE-Z
U1,U2,U3,U4 | AD5761ARUZ | 4 | 71.59 | 286.36 | Mouser (https://mouser.com/) | DAC | TSSOP-16_L5.0-W4.4-P0.65-LS6.4-TL
U5,U6,U7,U8,U28 | ADR421BRZ-REEL7 | 5 | 36.44 | 182.2 | LCSC (https://www.szlcsc.com/) | Voltage Reference | SOIC-8_L4.9-W3.9-P1.27-LS6.0-BL
U9,U10 | OPA2227UA/2K5 | 2 | 58.64 | 117.28 | LCSC (https://www.szlcsc.com/) | Opamp | SOIC-8_L4.9-W3.9-P1.27-LS6.0-BL
U11 | ADS8685IPWR | 1 | 59.87 | 59.87 | Mouser (https://mouser.com/) | ADC | TSSOP-16_L5.0-W4.4-P0.65-LS6.4-TL
U12, 21 | AD8671ARZ-REEL7 | 2 | 15.2 | 30.4 | LCSC (https://www.szlcsc.com/) | Opamp | SOIC-8_L4.9-W3.9-P1.27-LS6.0-BL
U27 | AD5721RBRUZ-RL7 | 1 | 84.27 | 84.27 | LCSC (https://www.szlcsc.com/) | DAC | TSSOP-16_L5.0-W4.4-P0.65-LS6.4-BL
 |  |  | TOTAL | 787.4605

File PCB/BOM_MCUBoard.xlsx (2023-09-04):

Designator | Component | Number | Cost per unit -CNY | Total cost -CNY | Source of materials | Material type | Footprint | Value
C1,C11 | CL10B104KA8NNNC | 2 | 0.02 | 0.04 | LCSC (https://www.szlcsc.com/) | Capacotor | C0603 | 100nF
C2,C10 | GRM188R61E106MA73D | 2 | 0.16 | 0.32 | LCSC (https://www.szlcsc.com/) | Capacotor | C0603 | 10uF
C9,C16 | CC0603KRX7R9BB104 | 2 | 0.01 | 0.02 | LCSC | Capacotor | C0603 | 100nF
C17,C18 | CL10A106MP8NNNC | 2 | 0.04 | 0.08 | LCSC | Capacotor | C0603 | 10uF
CN1 | X9555WR-2x07-6TV01 | 1 | 1 | 1 | LCSC | Connector | CONN-TH_14P-P2.54_XKB_X9555WR-2X7-6TV01
CN2 | XT30PW-M | 1 | 2.22 | 2.22 | LCSC | Connector | CONN-TH_XT30PW-M
H1,H2,H4,H5 | B-2100S02P-A110 | 4 | 0.14 | 0.56 | LCSC | Connector | HDR-TH_2P-P2.54-V-M-1
LED1,LED2 | 19-217/R6C-AL1M2VY/3T | 2 | 0.1 | 0.2 | LCSC | LED | LED0603-RD_BLUE
Q1,Q2 | S8050LT1J3Y | 2 | 0.05 | 0.1 | LCSC | BJT | SOT-23-3_L2.9-W1.3-P1.90-LS2.4-BR
R1,R2,R3,R4,R5,R7,R8 | RC0603JR-0710KL | 7 | 0.0063 | 0.0441 | LCSC | Resistor | R0603 | 10k
R6,R9,R10,R11 | 0603WAF5101T5E | 4 | 0.006 | 0.024 | LCSC | Resistor | R0603 | 5.1kΩ
RF8 | BWSMA-KWE-Z001 | 1 | 2.77 | 2.77 | LCSC | Connector | SMA-TH_BWSMA-KWE-Z001
SW1 | K2-1817UQ-C4SW-01 | 1 | 0.73 | 0.73 | LCSC | Switch | KEY-SMD_2P-L6.0-W6.0-P6.00
U7 | CH340C | 1 | 2.99 | 2.99 | LCSC | USB to TTL chip | SOP-16_L10.0-W3.9-P1.27-LS6.0-BL
U9 | ME6217C33M5G | 1 | 0.52 | 0.52 | LCSC | LDO | SOT-23-5_L3.0-W1.7-P0.95-LS2.8-BR
U11 | ESP32-WROOM-32E-N8 | 1 | 22.96 | 22.96 | LCSC | MCU Module | WIFI-SMD_ESP32-WROOM-32E
USBC1,USBC2 | TYPE-C-31-M-12 | 2 | 1.35 | 2.7 | LCSC | Connector | USB-C_SMD-TYPE-C-31-M-12
 |  |  | TOTAL | 37.2871

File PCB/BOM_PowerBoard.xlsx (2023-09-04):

Designator | Component | Number | Cost per unit -CNY | Total cost -CNY | Source of materials | Material type | Footprint | Value
C1,C2,C3,C4,C5 | CL31A106KBHNNNE | 5 | 0.2 | 1 | Capacitor | LCSC (https://www.szlcsc.com/) | C1206 | 10uF
C6,C7 | CL10A105KL8NNNC | 2 | 0.1 | 0.2 | Capacitor | LCSC (https://www.szlcsc.com/) | C0603 | 1uF
C8,C9 | CL10B473KB8NNNC | 2 | 0.04 | 0.08 | Capacitor | LCSC | C0603 | 47nF
C10,C11,C16,C19,C22 | CL31B225KBHNNNE | 5 | 0.2 | 1 | Capacitor | LCSC | C1206 | 2.2uF
C12,C29,C31,C32,C33 | CC0603KRX7R9BB104 | 5 | 0.01 | 0.05 | Capacitor | LCSC | C0603 | 100nF
C23,C25,C26,C27,C28 | T491A225M016AT | 5 | 0.4 | 2 | Capacitor | LCSC | CAP-SMD_L3.2-W1.6 | 2.2uF
D1,D2 | DFLS240-7 | 2 | 0.43 | 0.86 | Diode | LCSC | POWERDI-123_L2.8-W1.8-LS3.7-RD
D3 | MMSZ5233B-7-F | 1 | 0.21 | 0.21 | Diode | LCSC | SOD-123_L2.7-W1.6-LS3.7-RD
H1,H2,H4,H5,H6,H8,H9 | PM254V-11-03-H85 | 7 | 0.57 | 3.99 | Connector | LCSC | HDR-TH_3P-P2.54-V-F
H3,H7,H10,H11,H12,H13,H14 | PZ254V-11-02P | 7 | 0.08 | 0.56 | Connector | LCSC | HDR-TH_2P-P2.54-V-F
L1 | MWSA0503S-4R7MT | 1 | 0.8 | 0.8 | Inductor | LCSC | IND-SMD_L5.4-W5.2 | 4.7uH
L2 | MWSA0603S-6R8MT | 1 | 0.6 | 0.6 | Inductor | LCSC | IND-SMD_L7.0-W6.6 | 6.8uH
R1 | RS-03L2434FT | 1 | 0.006 | 0.006 | Resistor | LCSC | R0603 | 2.43MΩ
R2 | 0603WAF1373T5E | 1 | 0.006 | 0.006 | Resistor | LCSC | R0603 | 137kΩ
R3 | ERJ3EKF1183V | 1 | 0.06 | 0.06 | Resistor | LCSC | R0603 | 118kΩ
R4 | RC0603FR-072M32L | 1 | 0.02 | 0.02 | Resistor | LCSC | R0603 | 2.32MΩ
R5,R11,R20 | 0603WAF1002T5E | 3 | 0.005 | 0.015 | Resistor | LCSC | R0603 | 10kΩ
R6,R14,R23,R25,R26 | 0603WAF0000T5E | 5 | 0.006 | 0.03 | Resistor | LCSC | R0603 | 0Ω
R7 | 0603WAF1432T5E | 1 | 0.006 | 0.006 | Resistor | LCSC | R0603 | 14.3kΩ
R8 | 0603WAF1102T5E | 1 | 0.006 | 0.006 | Resistor | LCSC | R0603 | 11kΩ
R9 | 0603WAF4992T5E | 1 | 0.006 | 0.006 | Resistor | LCSC | R0603 | 49.9kΩ
R10 | 0603WAF1202T5E | 1 | 0.006 | 0.006 | Resistor | LCSC | R0603 | 12kΩ
R12,R21 | 0603WAF9102T5E | 2 | 0.006 | 0.012 | Resistor | LCSC | R0603 | 91kΩ
R13,R22,R24 | 0603WAF1001T5E | 3 | 0.004 | 0.012 | Resistor | LCSC | R0603 | 1kΩ
R15,R27 | 0603WAF5232T5E | 2 | 0.006 | 0.012 | Resistor | LCSC | R0603 | 52.3kΩ
R16,R28 | 0603WAF5901T5E | 2 | 0.006 | 0.012 | Resistor | LCSC | R0603 | 5.9kΩ
R17,R29 | 0603WAF6190T5E | 2 | 0.006 | 0.012 | Resistor | LCSC | R0603 | 619Ω
R18 | 0603WAF3162T5E | 1 | 0.006 | 0.006 | Resistor | LCSC | R0603 | 31.6k
R19 | 0603WAF1002T5E | 1 | 0.005 | 0.005 | Resistor | LCSC | R0603 | 10k
RF1,RF2,RF3,RF4,RF5,RF6,RF7,RF8 | BWSMA-KWE-Z001 | 8 | 2.77 | 22.16 | Connector | LCSC | SMA-TH_BWSMA-KWE-Z001
U1 | ADP5070ACPZ-R7 | 1 | 18.9 | 18.9 | DC-DC Chip | LCSC | LFCSP-20_L4.0-W4.0-P0.50-TL-EP2.6
U2,U4,U5 | ADP7118AUJZ-R7 | 3 | 10.42 | 31.26 | Low noise LDO | LCSC | TSOT-23-5_L2.9-W1.6-P0.95-LS2.8-BR
U3,U6 | ADP7182AUJZ-R7 | 2 | 13.46 | 26.92 | Low noise LDO | LCSC | TSOT-23-5_L2.9-W1.6-P0.95-LS2.8-BR
 |  |  | TOTAL | 110.822

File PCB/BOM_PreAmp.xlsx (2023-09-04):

Designator | Component | Number | Cost per unit -CNY | Total cost -CNY | Source of materials | Material type | Footprint | Value
C1,C3,C4,C6 | CC0603KRX7R9BB104 | 4 | 0.01 | 0.04 |  | LCSC (https://www.szlcsc.com/) | C0603 | 100nF
C2,C5 | C2012X5R1V226MT000E | 2 | 1.43 | 2.86 |  | LCSC (https://www.szlcsc.com/) | C0805 | 22uF
C7 | 0402CG5R0C500NT | 1 | 0.006 | 0.006 |  | LCSC | C0402 | 5pF
FPC1 | THD0510-05CL-GF | 1 | 0.64 | 0.64 |  | LCSC | FPC-SMD_5P-P0.50_THD0510-05CL-GF
R1 | HMC0603JT100M | 1 | 0.65 | 0.65 |  | LCSC | R0603 | 100M
R2 | 0402WGF2200TCE | 1 | 0.003 | 0.003 |  | LCSC | R0402 | 220Ω
U2 | OPA627AU/2K5 | 1 | 233.42 | 233.42 |  | Mouser (https://mouser.com/) | SOIC-8_L5.0-W4.0-P1.27-LS6.0-BL
 |  |  | TOTAL | 237.619

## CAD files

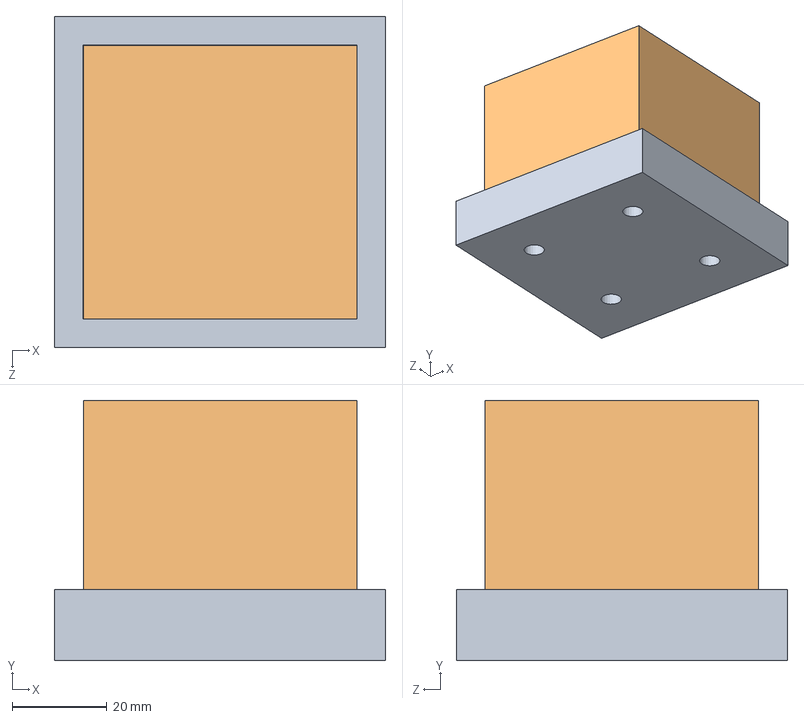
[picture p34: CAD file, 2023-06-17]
3DModels/Solidworks/Shell.SLDASM
70.0 x 55.0 x 70.0 mm
Shell_cover

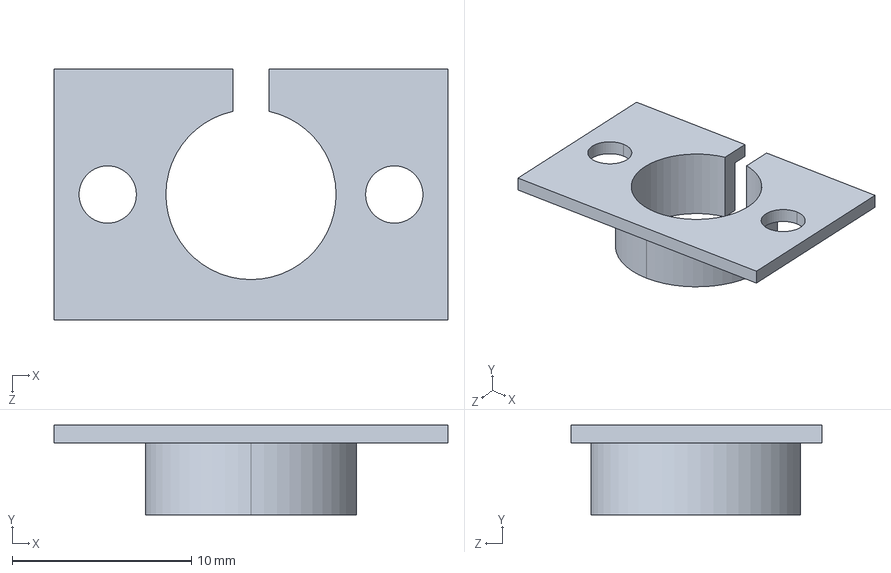
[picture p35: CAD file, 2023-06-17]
3DModels/CNC/Scanner_cover.STEP
22.0 x 5.00 x 14.0 mm

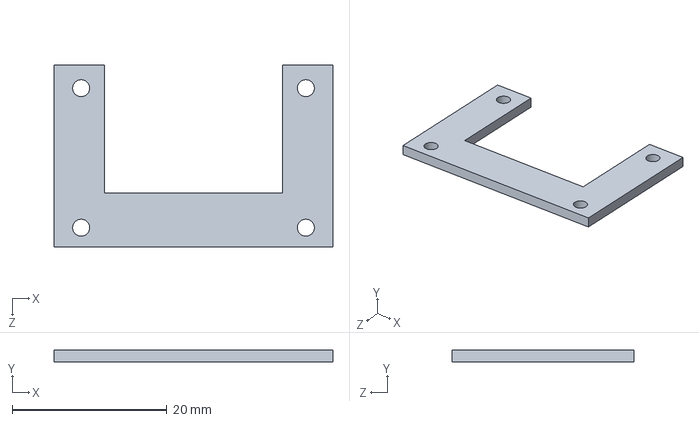
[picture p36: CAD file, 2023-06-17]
3DModels/Solidworks/PCB_Conncet.SLDPRT
36.0 x 1.60 x 23.5 mm

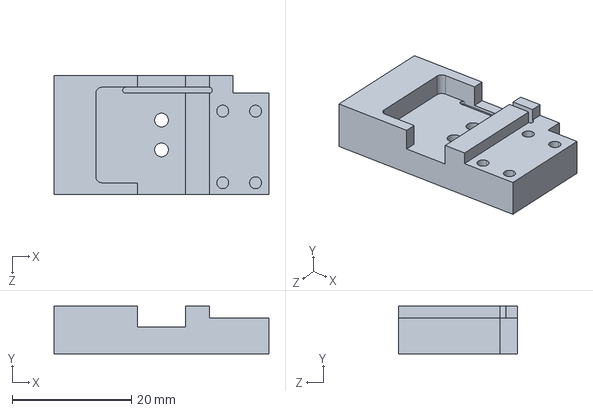
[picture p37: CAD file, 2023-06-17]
3DModels/CNC/PZM_Base.STEP
36.0 x 8.00 x 20.0 mm

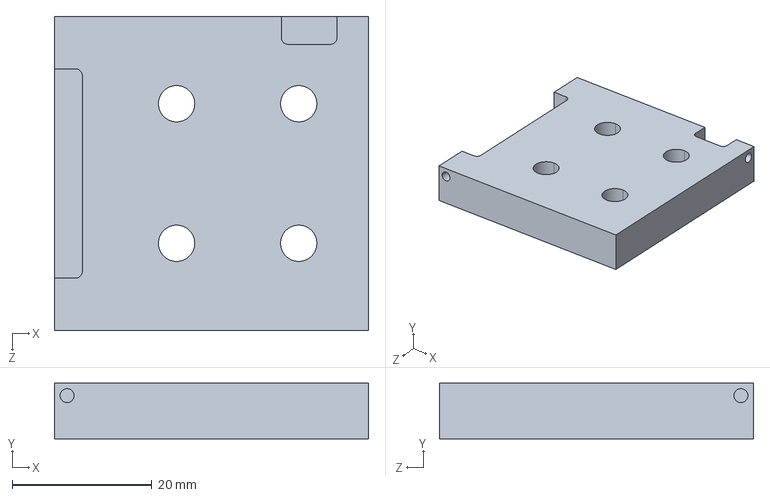
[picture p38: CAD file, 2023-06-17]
3DModels/CNC/Base.STEP
45.0 x 8.00 x 45.0 mm

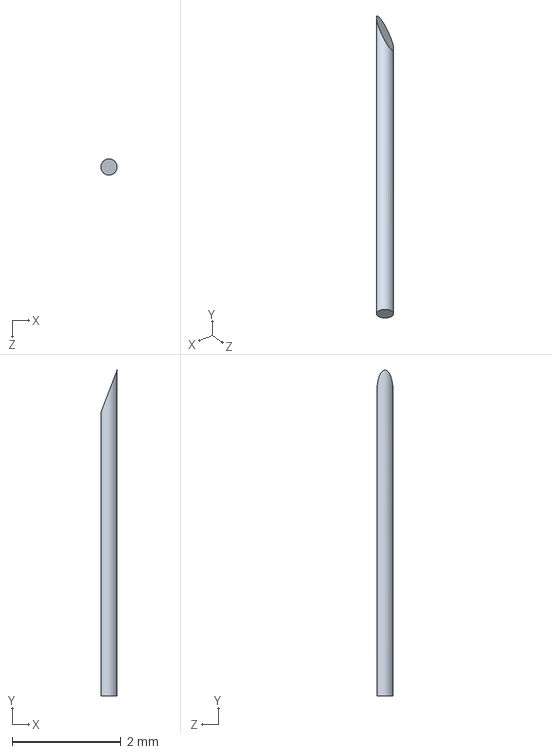
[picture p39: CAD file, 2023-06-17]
3DModels/Solidworks/tip.SLDPRT
0.3 x 6.00 x 0.3 mm

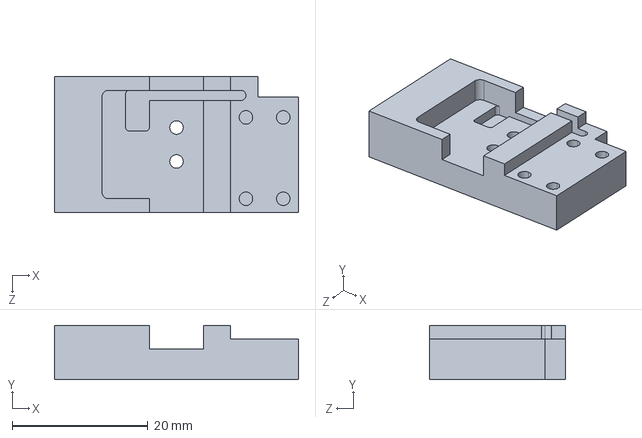
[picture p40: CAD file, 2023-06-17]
3DModels/CNC/PZM_Base_extend.STEP
36.0 x 8.00 x 20.0 mm

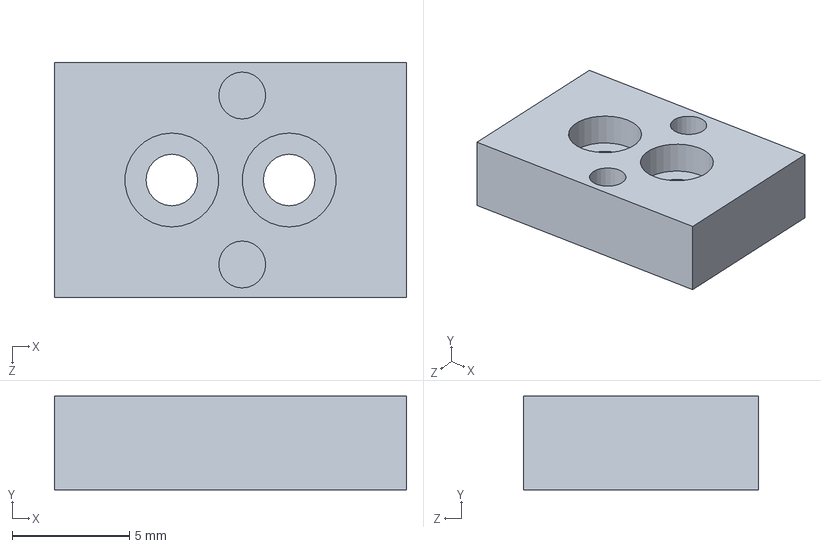
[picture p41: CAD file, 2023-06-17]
3DModels/Solidworks/SAMPLE_TABLE.SLDPRT
15.0 x 4.00 x 10.0 mm

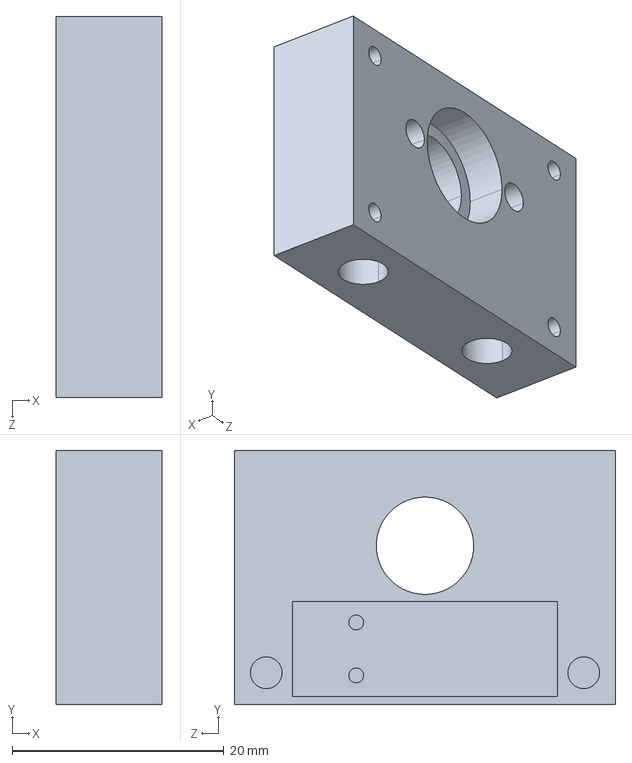
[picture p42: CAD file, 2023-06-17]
3DModels/CNC/Scanner_Mount.STEP
10.0 x 24.0 x 36.0 mm

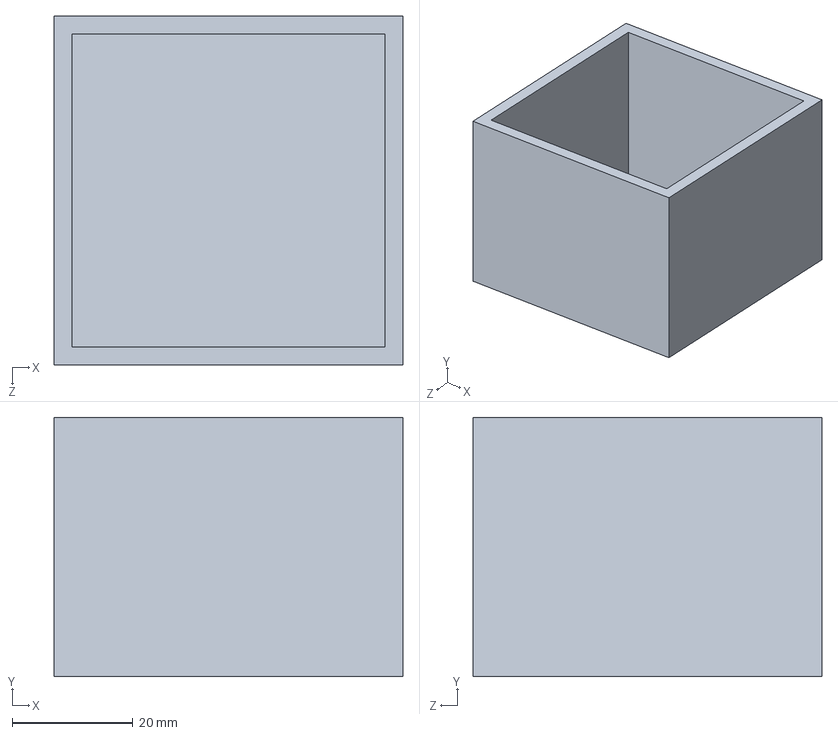
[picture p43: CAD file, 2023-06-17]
3DModels/Solidworks/Shell_cover.SLDPRT
57.9 x 43.0 x 57.9 mm

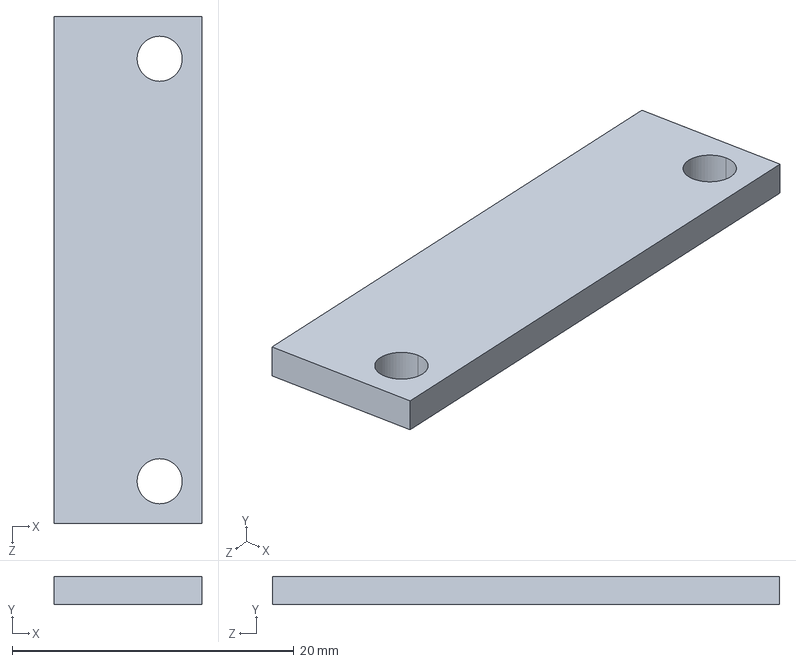
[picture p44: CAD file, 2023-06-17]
3DModels/CNC/Preamp_cover.STEP
10.5 x 2.00 x 36.0 mm

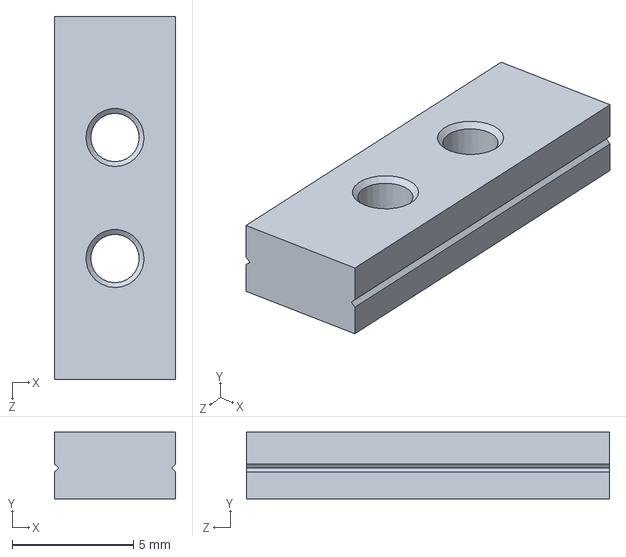
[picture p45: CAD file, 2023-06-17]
3DModels/Solidworks/Slider_Bottom.SLDPRT
5.00 x 2.75 x 15.0 mm

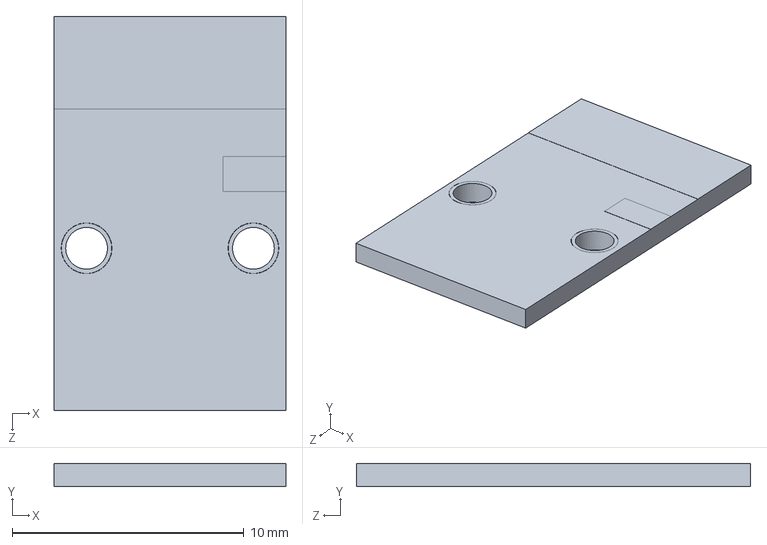
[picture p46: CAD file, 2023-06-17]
3DModels/Solidworks/sample_PCB.SLDPRT
10.0 x 1.01 x 17.0 mm

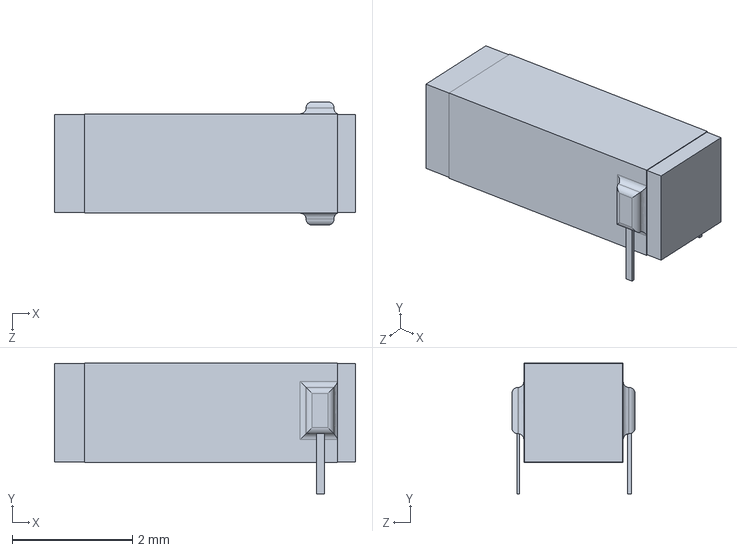
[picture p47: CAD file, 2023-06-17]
3DModels/Solidworks/pzt.SLDPRT
5.00 x 2.17 x 2.05 mm

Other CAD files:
3DModels/CNC/Sample_Table.STEP
3DModels/Solidworks/Scanner_Mount.SLDPRT
3DModels/Solidworks/connector_PCB.SLDPRT
3DModels/3DPrint/Shell.STL
3DModels/3DPrint/Shell_cover.STL
3DModels/Solidworks/PCB_Connect_component.SLDPRT
3DModels/Solidworks/PZM_BASE.SLDPRT
3DModels/Solidworks/PZM_BASE_NO_EXTEND.SLDPRT
3DModels/Solidworks/PiezoCrystal.SLDPRT
3DModels/Solidworks/Preamp_cover.SLDPRT
3DModels/Solidworks/Scanner_cover.SLDPRT
3DModels/Solidworks/Shell.SLDPRT
3DModels/Solidworks/Slider.SLDPRT
3DModels/Solidworks/Slider_up.SLDPRT
3DModels/Solidworks/base.SLDPRT
3DModels/Solidworks/connector_PCB_component.SLDPRT
3DModels/Solidworks/magnent.SLDPRT
3DModels/Solidworks/magnent_10x2x5.SLDPRT
3DModels/Solidworks/pcb_tip_mount.SLDPRT
3DModels/Solidworks/preamp_component.SLDPRT
3DModels/Solidworks/round_megnent.SLDPRT
3DModels/Solidworks/screw_M2-12.SLDPRT
3DModels/Solidworks/screw_M2-3.SLDPRT
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

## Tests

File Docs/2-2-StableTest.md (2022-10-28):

# 电流稳定性评估

## 仅二级减震系统下的评估

        稳定的隧穿电流为显微镜的成像质量以及曲线测量提供了最基本的保障。在显微镜建立隧穿电流后，使扫描头动作停止，通过监测隧穿电流随时间变化情况可以进行电流稳定性评估,通过该评估可以简单分析震动以及热漂移对隧穿电流的影响。

        下图为样品偏置电压为50mV下，仅使用二级减震系统时，时长为733秒的测试结果。从图中可以看出，在733秒内，输出的隧穿电流值在40nA附近浮动，且整体波动幅度较大，最大值出现在601.55秒处，大小为55.8nA，最小值出现在347秒处，大小为31.3nA。对于隧穿电流整体的大幅度波动，可能是由于热膨胀导致，而对于小幅度的高频波动，可能是由于震动导致。

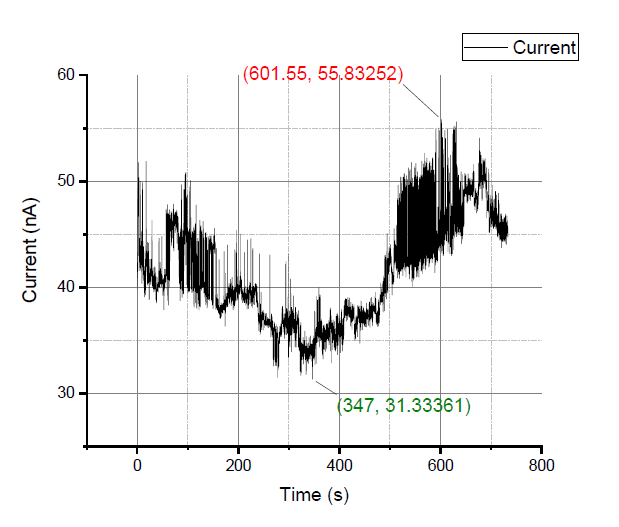
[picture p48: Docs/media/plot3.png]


        以扫描一副分辨率为256×256的图像为例，单点采样时间设置为500μs时，该幅图像的采样时间为32.768s。图中出现了多个持续时长大于30s且电流较为平稳的区间，以364s至408s持续44秒的区间为例，其缩放后曲线如下图所示。在该区间内，极差为5.1722nA，对于随距离指数级变化的隧穿电流而言，该时间区间的电流变化是可以接受的。通过缩短单点采样的时间或减少采样点数量，可以进一步缩短图像扫描的时间，从而达到更稳定的图像。

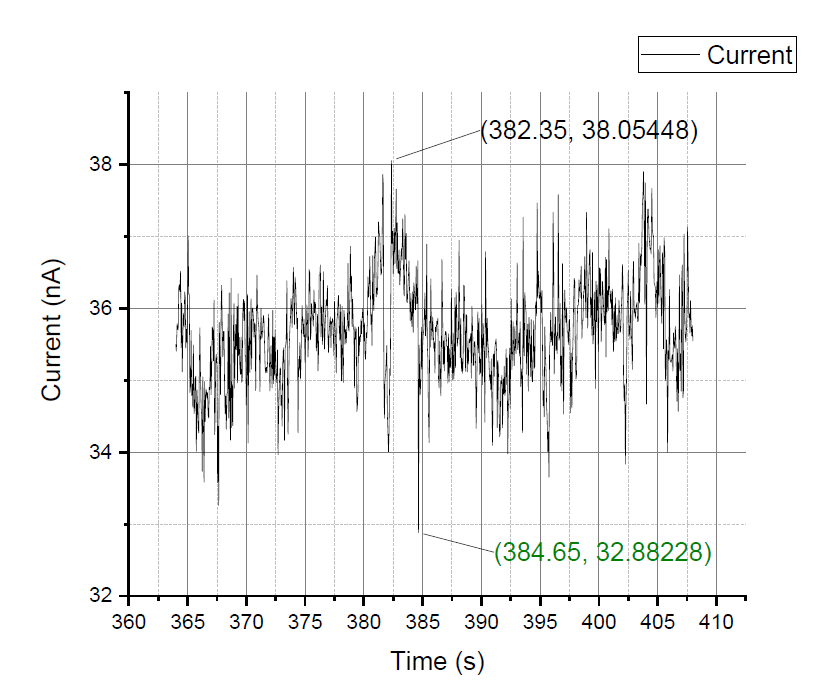
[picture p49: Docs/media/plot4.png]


## 完整减震系统下的评估

        下图为使用完整的二级减震系统下，时长为五分钟的测试结果。可以看出，相对于单第二级减震系统的测试环境，完整的二级减震系统对系统电流的稳定性有显著的提升。

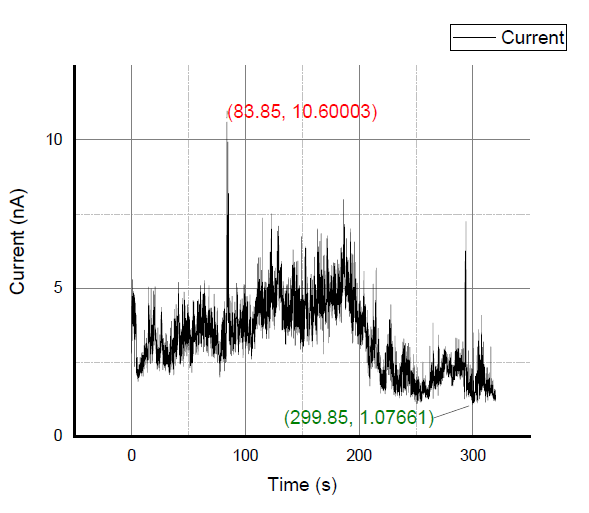
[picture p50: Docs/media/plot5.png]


        同样在该曲线中取44秒左右较平稳的时间段进行缩放，如下图所示，此时的极差被缩小至3.12nA。

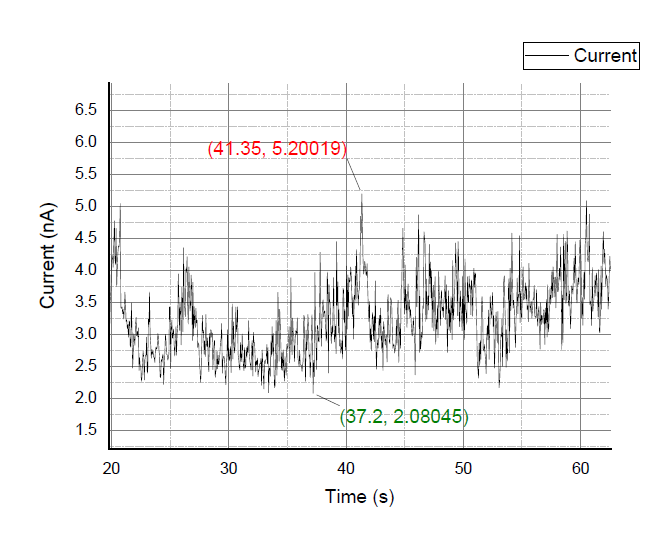
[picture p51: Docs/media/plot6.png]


## 结论

        在仅二级减震系统下，测试得到44秒区间内的电流变化曲线极差为5.1722nA。在完整减震系统下，测试得到44秒区间内的电流变化曲线极差为3.12nA。对于典型图像扫描所需时间32.768秒而言，在不同级别减震系统下的稳定性均可满足图像扫描的条件。同时测试也能够在一定程度上证明通过两级减震系统的结合，能够提升显微镜的稳定性。

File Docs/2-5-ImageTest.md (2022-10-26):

# 图像扫描测试

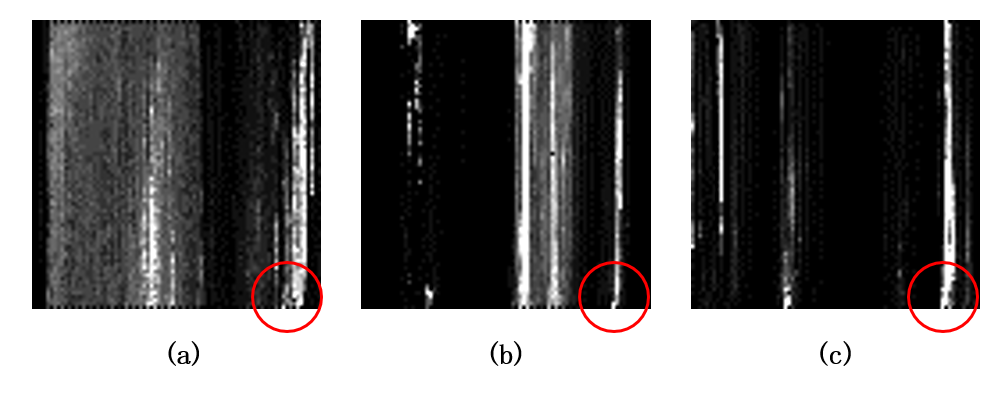
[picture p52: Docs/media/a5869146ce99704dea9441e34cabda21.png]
a5869146ce99704dea9441e34cabda21


        上图所示图像为偏置电压为500mV，扫描步长为18.5mV下对HOPG相同位置下的三次扫描结果，采样点数量为80×80。图像的高亮部分表示较大的隧穿电流，即形貌突起。在三次扫描结果的右下角均出现了细长状且带有弯曲的突起条带（如图红圈所示），在一定程度上证明了成像结果的可靠性。对于条带以外的非重复部分，可能是由于热漂移或震动产生的噪声导致。

        通过重复性测试，能够基本证明扫描图像的真实性。本项目原计划利用热解石墨（HOPG）的原子结构进行显微镜的放大倍数标定，虽然现搭建的显微镜系统具有一定的稳定性，但现有的隧道电流波动幅度对于原子级分辨率的图像仍然无法正常扫描成像。由于时间关系以及现有结构存在的部分缺陷（需要进行结构重构），故本项目当前的样品成像仅能对样品表面进行无法标注具体尺寸的简单形貌扫描。

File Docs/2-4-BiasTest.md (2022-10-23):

# 偏压测试

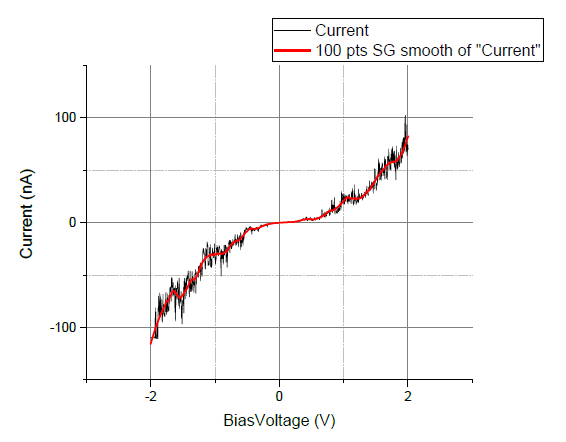
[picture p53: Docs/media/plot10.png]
plot10


        当探针与样品间距恒定时，通过改变偏置电压所测得的偏置电压-隧穿电流曲线测试得到的曲线与样品的表面电子态有一定的关系[27]，偏压-隧穿电流曲线取一阶微分将能够得到扫描隧道谱曲线[1]。

        图4.9为扫描头恒定高度时，HOPG（高定向热解石墨）样品的偏压曲线，偏置电压间隔为3.1mV，其中黑色曲线为原始数据，红色曲线为平滑曲线。从曲线特征中可以看出，通过与其他研究人员的偏压曲线进行对比[2][3]，可初步认为本项目所测曲线满足一定的HOPG样品特征。

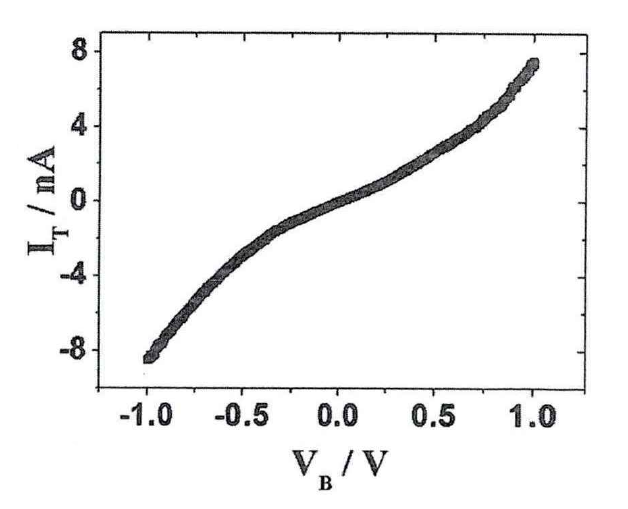
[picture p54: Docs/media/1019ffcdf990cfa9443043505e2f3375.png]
1019ffcdf990cfa9443043505e2f3375


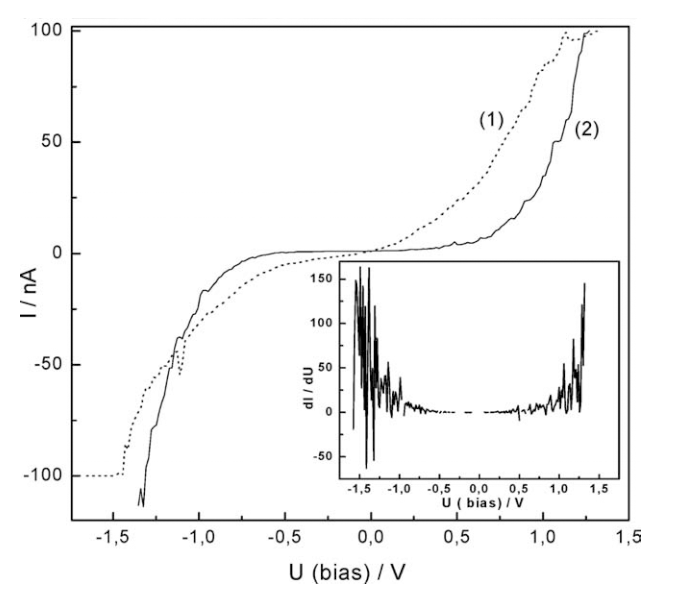
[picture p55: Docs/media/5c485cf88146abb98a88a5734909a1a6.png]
5c485cf88146abb98a88a5734909a1a6


# 参考文献

[1].    Chen C J. Theory of scanning tunneling spectroscopy[J]. Journal of Vacuum Science & Technology A: Vacuum, Surfaces, and Films, 1988, 6(2): 319-322.

[2].    王琦. 高稳定扫描隧道显微镜的研制与应用[D].  中国科学技术大学,2014.

[3].    El Abedin S Z, Borissenko N, Endres F. Electrodeposition of nanoscale silicon in a room temperature ionic liquid[J]. Electrochemistry communications, 2004, 6(5): 510-514.

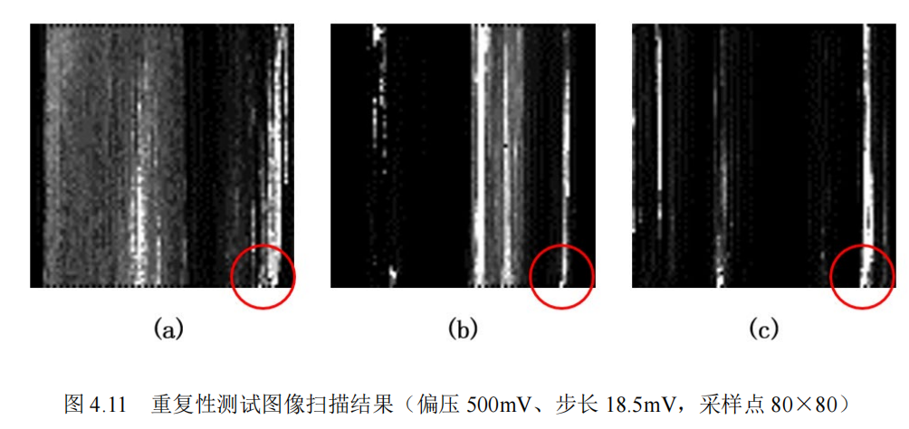
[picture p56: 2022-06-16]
readme_image/repeat_test.png

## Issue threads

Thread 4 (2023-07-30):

### ISSUE TITLE
您好，请教一下薛定谔方程的问题

### ISSUE THREAD

**Issue by testf123** [Dimsmary/OpenSTM#4]
您好，项目不错，我也在做，有个问题想请教一下：
您的文档中，关于薛定谔方程的描述，
![1](https://github.com/Dimsmary/OpenSTM/assets/109737894/8539e94c-d6b8-4ac8-901e-d1d4653c3b6a)

这个与我的理解不一样，我认为应该是这个：
![2](https://github.com/Dimsmary/OpenSTM/assets/109737894/c0a0fa77-1f69-43da-b90f-ff97b3cc5aa9)

尽管不影响最后的结果，因为在V=0的情况下，下文的假设使得前面2个方程都行得通：
![3](https://github.com/Dimsmary/OpenSTM/assets/109737894/e000a159-793b-4d13-9892-246d7ea1865f)

您认为呢？

**Comment by Dimsmary** [comment]
在公式编辑时弄反了，你的公式是正确的，已修正。

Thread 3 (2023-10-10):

### ISSUE TITLE
Question

### ISSUE THREAD

**Issue by GongJiaBao** [Dimsmary/OpenSTM#3]
可以放出细小零件规格么，例如弹簧

**Comment by Dimsmary** [comment]
目前还在完善技术文档，文档完善后将包括此内容

**Comment by Daivdwang555** [comment]
大佬您好。我们观看了您自制扫描隧道显微镜的视频，想要参照您的电路做一个复刻，但发现AD5761RBRUZ、ADS8685IPWR、ATMEGA328P-MU这三款芯片好像搜不到货源，买不到。想问一下大佬有没有什么解决的方法?

**Comment by Aurora000111** [comment]
好的大佬，留下足迹，我开始复刻了

**Comment by Aurora000111** [comment]
> 

看到这个真的太激动了

**Comment by Aurora000111** [comment]
好的大佬，留下足迹，我开始复刻了，看到这个真的太激动了
希望能将他改进的更有趣

**Comment by ybh618** [comment]
感谢大佬，Star了

**Comment by Anwen758** [comment]
准备开始复现，star先

**Comment by lyqqhgzj** [comment]
B站热门，先star，等完善以后，看看作为一个门外汉能否也复现一下

**Comment by Tain39** [comment]
紧跟大佬的脚步，准备复现一个

**Comment by kurt021** [comment]
太酷了，准备复现一个

**Comment by SiyuanZhangGit** [comment]
留名复现！~！！

**Comment by Dimsmary** [comment]
技术文档已发布，请参阅最新readme，或访问：https://arxiv.org/abs/2310.05413

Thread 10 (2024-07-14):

### ISSUE TITLE
看过你的视频和项目好几遍了，这次再细看电路，看出一点强迫症

### ISSUE THREAD

**Issue by Staok** [Dimsmary/OpenSTM#10]
首先，up可能对硬件还少一些实战的经验，这个大多数硬件玩家的遗憾，指出一些问题，纯属当我强迫症罢：
1、芯片的选型很迷，比如DC-DC、Vref参考基准、ADC，还有关键的运放，选的都是死贵死贵的（JLC估计可开心了）又比较老的（有年头的），而且可能不需要高带宽的运放选了，可能Δ-Σ的ADC更好而选择了SAR，TIA电路的跨阻电阻可以选择金属膜的噪声更低（这是TIA电路在业界的普遍认识），选型的门道也很多，一是芯片的调研和使用经验少点，另一个是受到很多国内外的开源项目的选型的影响（很多高性价比的方案都没有开源都是发烧友自己设计的，开源出来的大都很少有货真价实的高性价比的良品），所以这个项目不适合直接供他人打板买芯片然后SMT，成本太太高（富哥除外），适合那些有经验的在你的基础上再优化优化选型和电路等（然后他们选择不开源hhh）。
2、电路的拓扑设计可以更好，比如产生负压的方案，降低噪声纹波的方案，这里面门道需要多看多试验都少不了。然后PCB的走线，尤其是电源部分的噪声控制，我不知道你实际测过纹波没有。然后以上如果深度优化下的话，估计出图效果会更好!

**Comment by Dimsmary** [comment]
抱歉，整个项目都是我个人独立设计的，所以很难顾及所有方面，所以目前所有的设计都是基于「能实现」的目的，而非「最优」的设计。

- 对于您提到的，芯片选型的问题，同样是基于此角度进行选型的。在选型时只是简单考虑了其纸面参数是否能够满足我的目的以及「我」本人是否能够承担其成本。对于外围芯片，如基准电压芯片同样也是基于DAC芯片的数据手册照搬而来。

- 至于您提到的电源纹波以及出图效果，目前我所用的设备精度难以测出ADP5070与ADP7182/7118输出的噪声，所以我暂时肤浅的认为电源部分是足以使用的。目前出图效果较差的原因我认为仍然是系统震动难以消除，这一部分可能可以采用更稳固的压电滑台设计，或提升ADC/DAC速度以解决。

- 但归根结底本项目只是一个爱好者的DIY项目，我无意顾及所有方面，开源也只是为了给想要DIY STM的爱好者提供多一种可选的方案。

但如果您有意优化本项目，也非常欢迎提供进一步的意见，谢谢。

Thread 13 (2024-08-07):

### ISSUE TITLE
您好，请问如果将音圈电机用于粗进近如何，我觉得可能有可行性

### ISSUE THREAD

**Issue by ZiRuiYu** [Dimsmary/OpenSTM#13]

**Comment by Dimsmary** [comment]
有考虑过，但是音圈电机需要在闭环的情况下才能达到比较高的精度，并且线圈发热可能是个问题？所以当时没有采用。不过我觉得音圈电机能通过某种形式解决这些问题的话，可以把音圈电机用于粗接近。

**Comment by ZiRuiYu** [comment]
好，谢谢

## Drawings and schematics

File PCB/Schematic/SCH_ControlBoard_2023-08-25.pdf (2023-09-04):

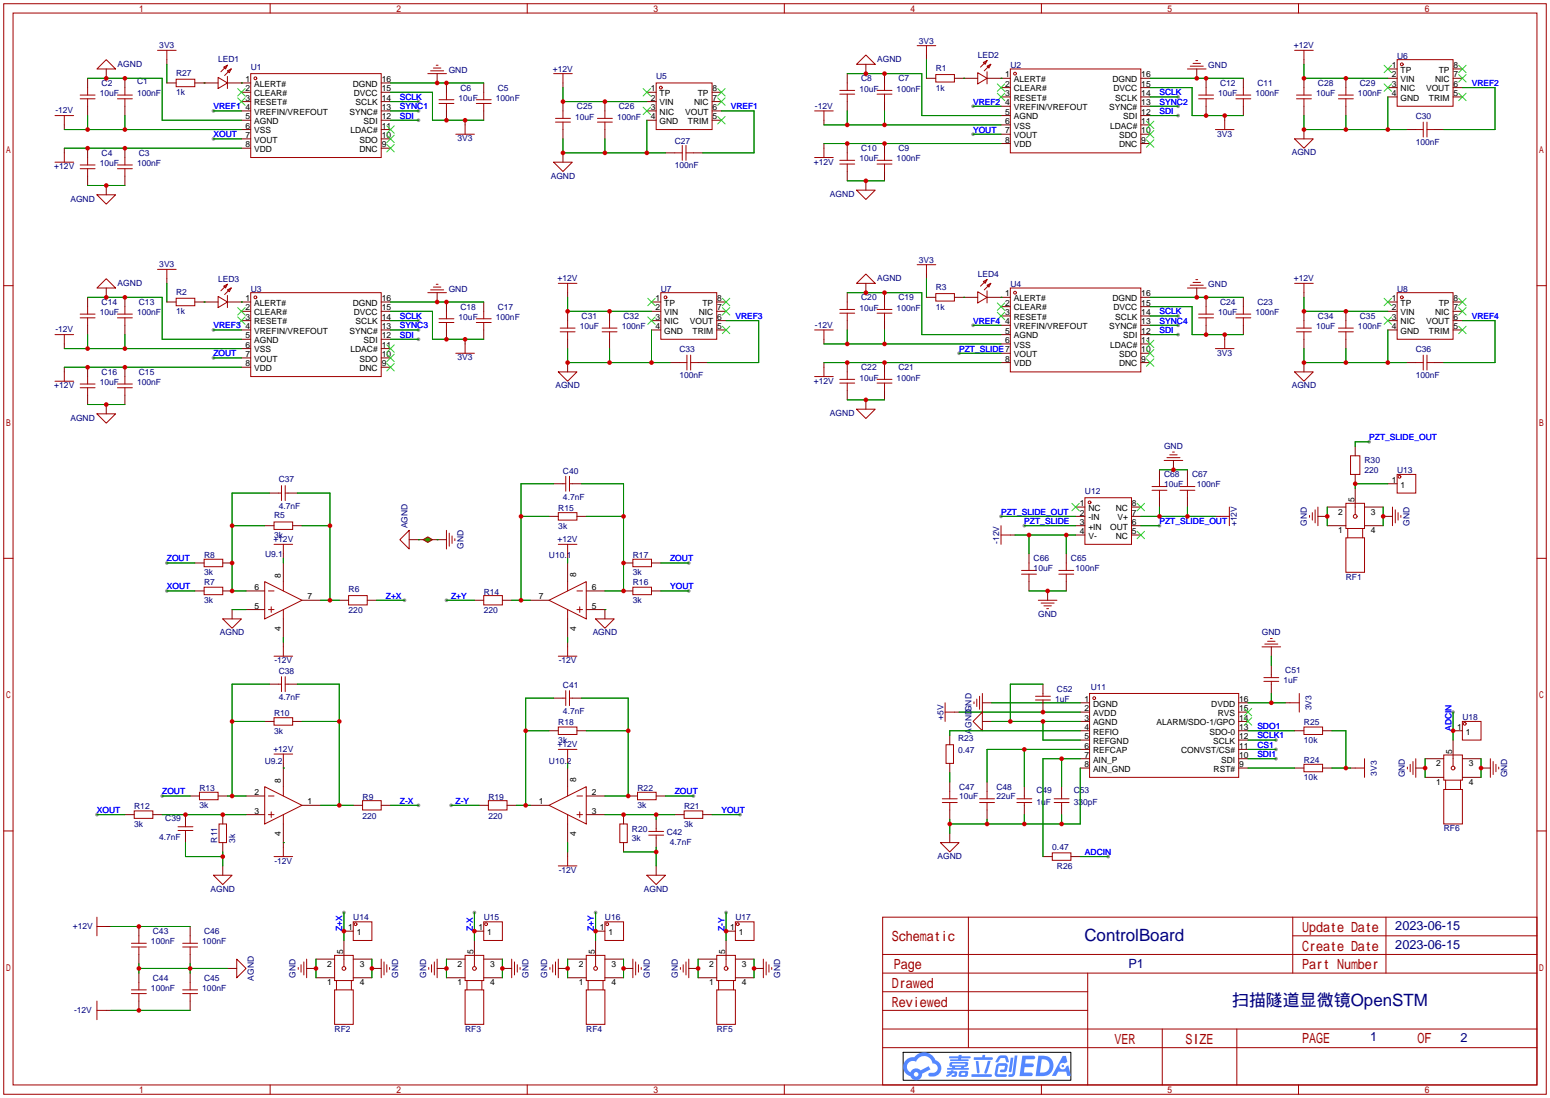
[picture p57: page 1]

SDO 10 LDAC# 11 SDI 12 SYNC# 13 SCLK 14 DVCC 15 DGND 16

SDI 10 CONVST/CS# 11 SCLK 12 SDO-0 13 ALARM/SDO-1/GPO 14 RVS 15 DVDD 16

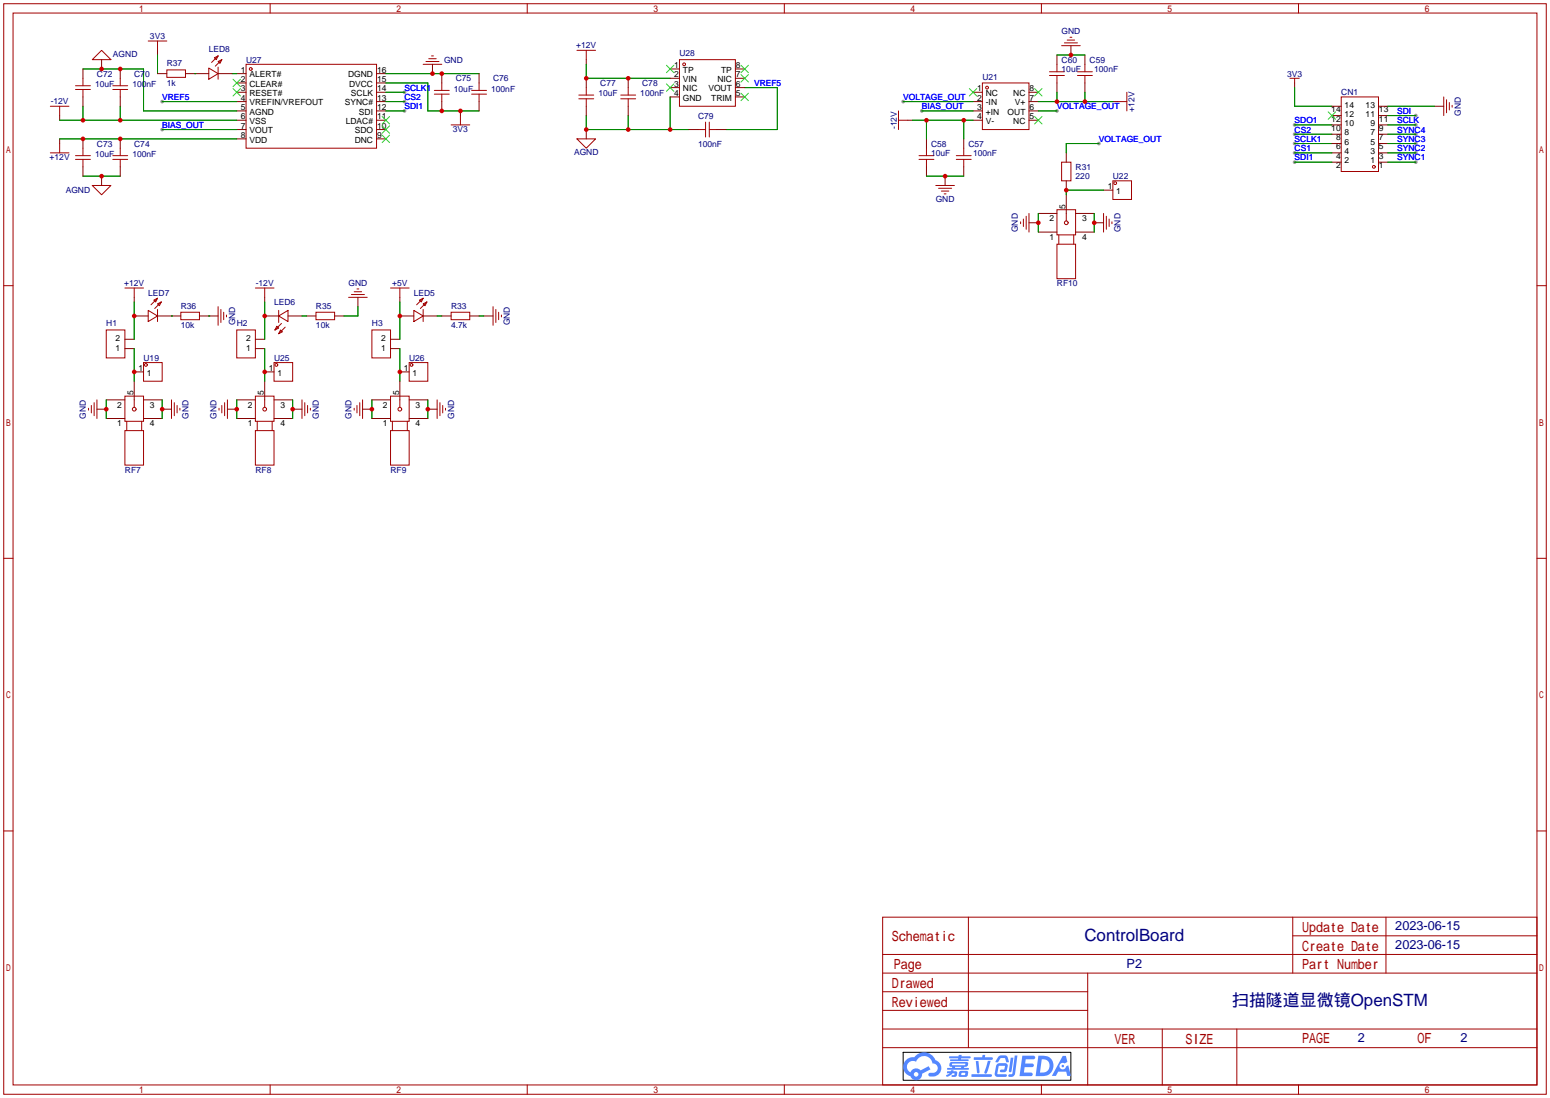
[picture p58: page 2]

SDO 10 LDAC# 11 SDI 12 SYNC# 13 SCLK 14 DVCC 15 DGND 16

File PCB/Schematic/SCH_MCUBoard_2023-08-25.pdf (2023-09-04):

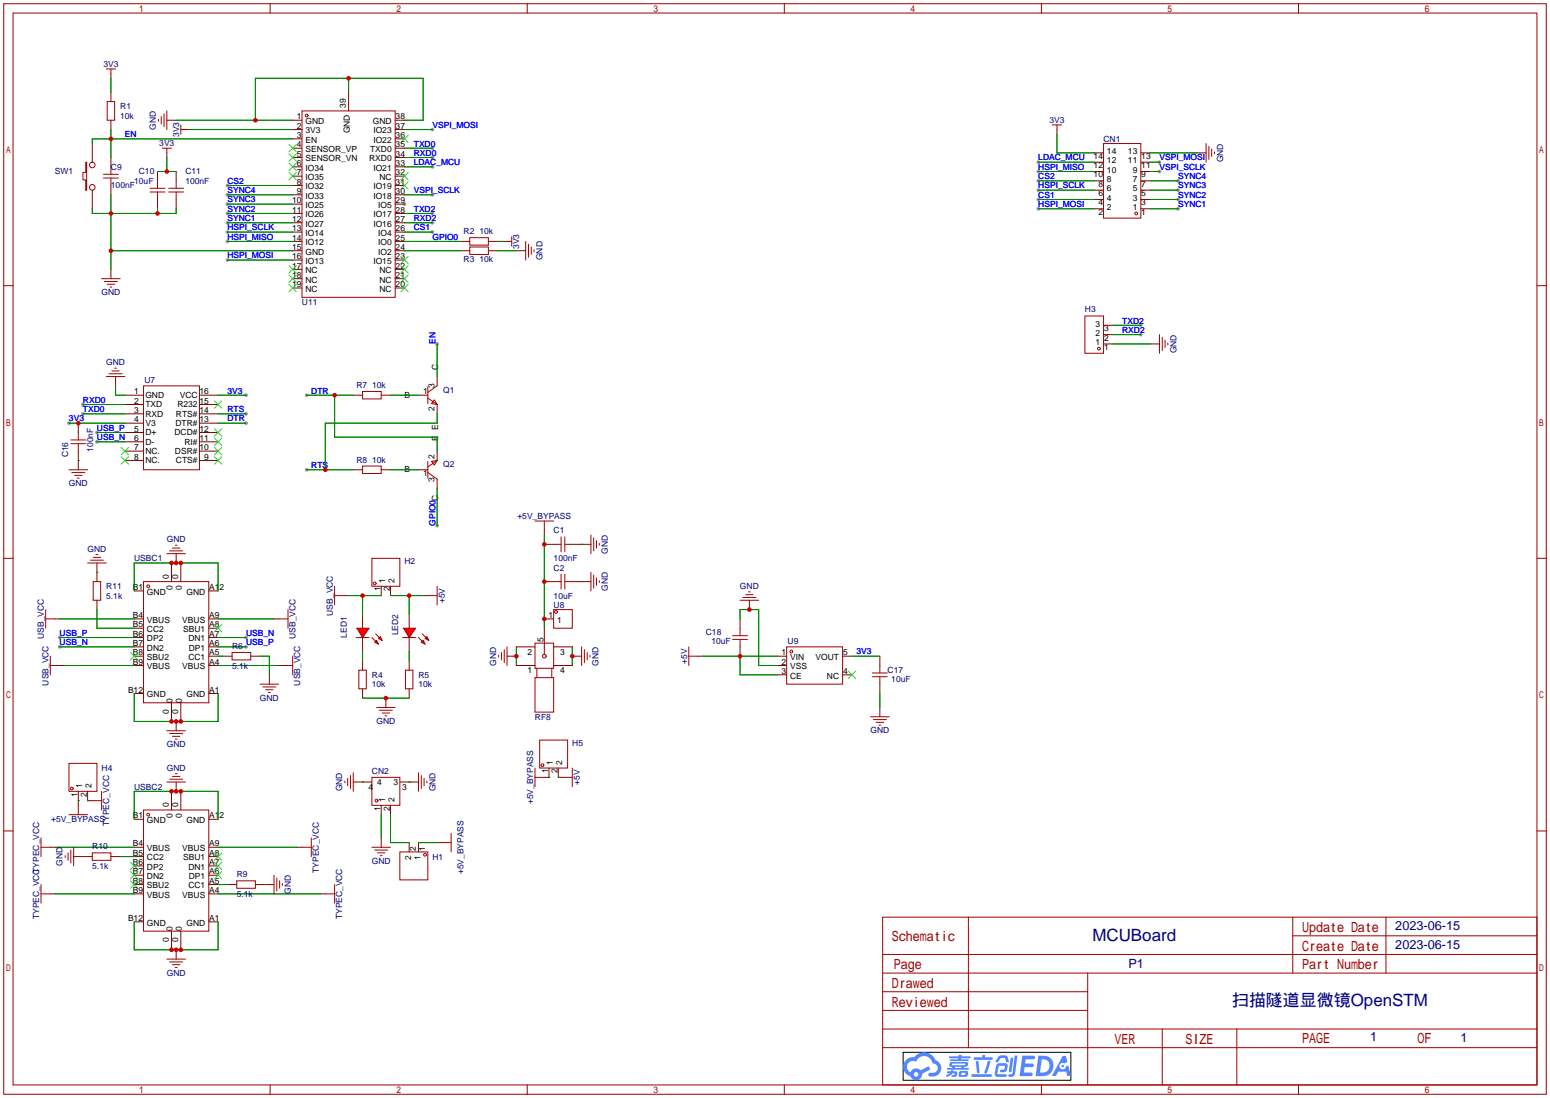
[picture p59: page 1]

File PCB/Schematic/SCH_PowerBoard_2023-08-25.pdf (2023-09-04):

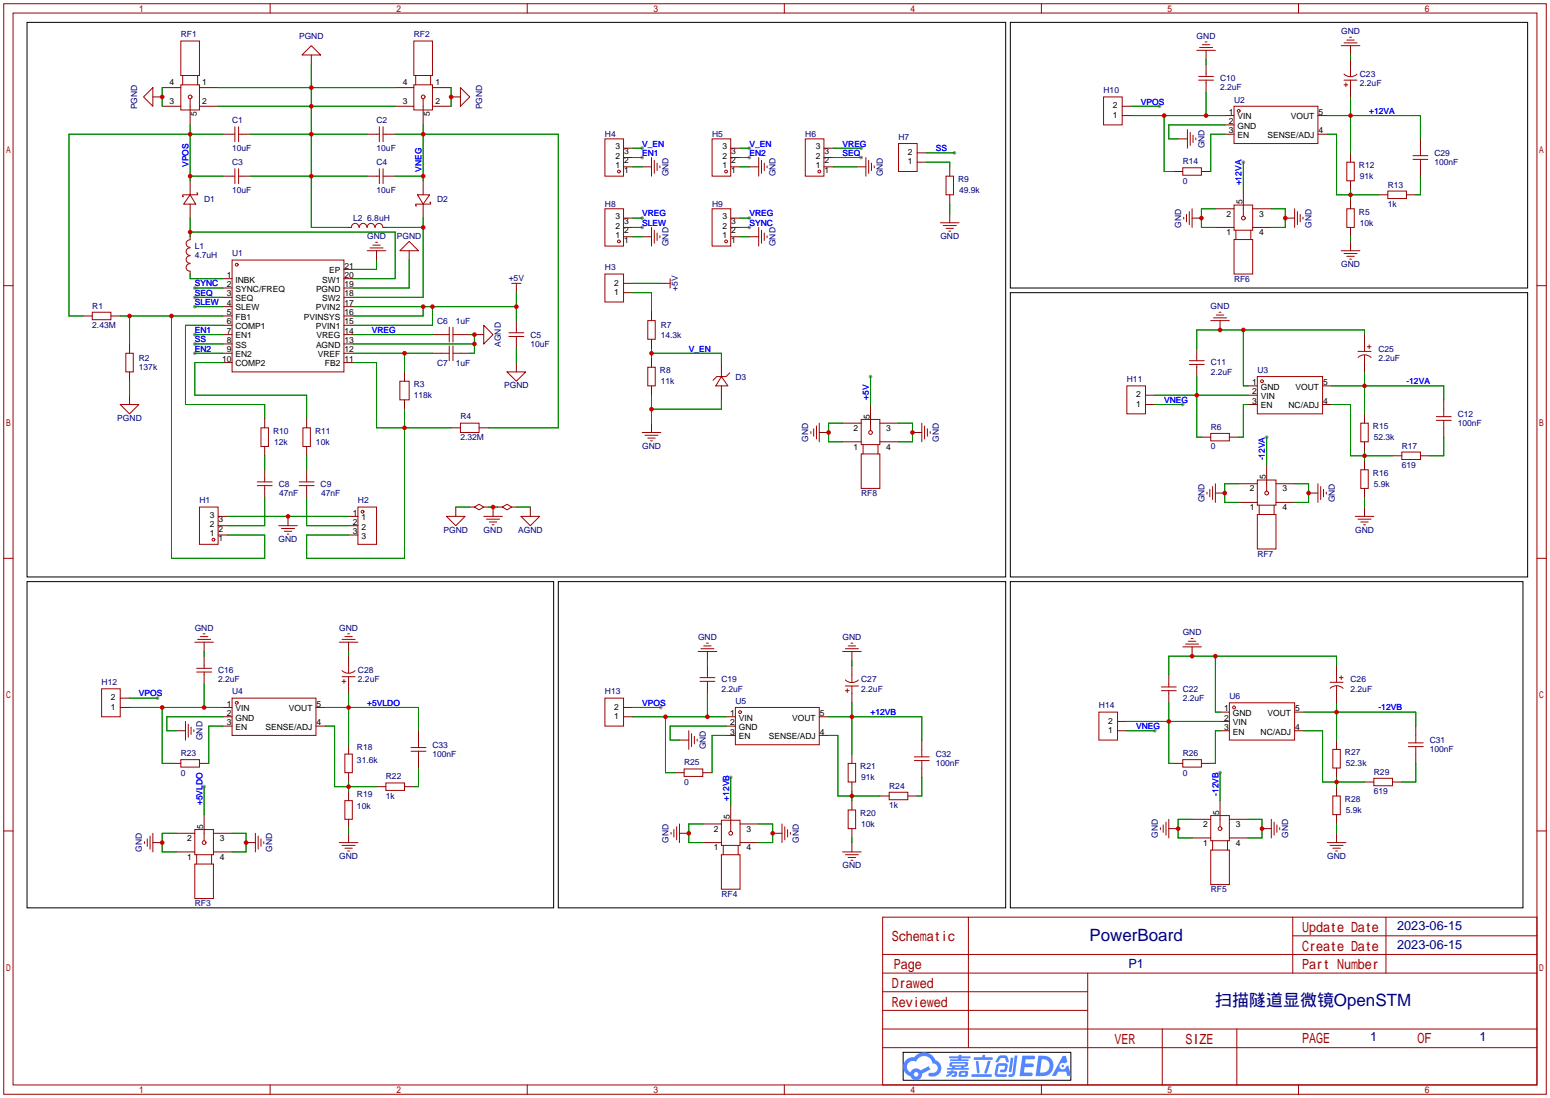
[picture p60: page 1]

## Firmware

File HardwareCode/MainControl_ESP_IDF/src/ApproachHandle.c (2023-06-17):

#include "ApproachHandle.h"

QueueHandle_t approach_handle_queue;
TaskHandle_t approach_handle;
int current_z_position = 0;
int target = 0;
float kp = 0.005;
float ki = 0;
float kd = 0;
int status = 0;
char output[50] = "";
int step = 10;
int crash = 0;
int err_acc = 0;
int err_last = 0;
int triangle_amplitude = 4095;
int triangle_slope = 16;
int cap_fast_limit = 0;
int cap_slow_limit = 0;
int bias_voltage = 0;

void approachH_init(){
    xTaskCreatePinnedToCore(approacH_task, "approach_handle_task", 
    1024*3, NULL, configMAX_PRIORITIES - PRIORITY_APPROACH_HANDLE, 
    &approach_handle, CORE_APPROACH);
}

int triangle_Wave_forward(int step, int amp, int inc){
    uint16_t data = 0;
    int read;
    // Generate Triangle Wave
    while(step > 0){
        data = 4095 - amp;
        while (data < 4095)
        {
            adda_12bitda_write(CMD_WR_UPDATE_DAC_REG, ~data << 4);
            data += inc;
        }
        
        data = 4095 - amp;
        adda_12bitda_write(CMD_WR_UPDATE_DAC_REG, ~data << 4);
        step --;
    }

    // measure voltage output
    read = adda_ad_write(ADS8689_NOP, 0, 0);
    read = adda_ad_write(ADS8689_NOP, 0, 0);

    // turn the 16bit data into binary
    read = read - 32768;

    // get absolute number of read
    if (read < 0)
    {
        read = -read;
    }
    return read;
}

void triangle_Wave_backward(int step, int amp, int inc){
    uint16_t data;
    // Generate Triangle Wave
    while(step > 0){
        data = 4095 - amp;
        while (data < 4095)
        {
            adda_12bitda_write(CMD_WR_UPDATE_DAC_REG, data << 4);
            data += inc;
        }
        
        data = 4095 - amp;
        adda_12bitda_write(CMD_WR_UPDATE_DAC_REG, data << 4);
        step --;
    }
        
}

bool z_scan(int target){
    // init z position is 0, tip retract
    int z_position = 0;
    ad5761_write(CMD_WR_UPDATE_DAC_REG, z_position, DA_Z);
    while (1)
    {   
        // Read adc
        int read = adda_ad_write(ADS8689_NOP, 0, 0);
        read = adda_ad_write(ADS8689_NOP, 0, 0);

        // remapping the read value
        read = read - 32768;
        if(read < 0){
            read = -read;
        }

        if(read < target){
            z_position = z_position + 50;
            if(z_position > 65535){
                return false;
            }
            ad5761_write(CMD_WR_UPDATE_DAC_REG, z_position, DA_Z);
            vTaskDelay(1);
        }
        else{
            //recored current Z position
            current_z_position = z_position;
            return true;
        }
        
    }
}

void approacH_task(void *arg){
    approach_handle_queue = xQueueCreate(APPROACH_QUEUE_LENGTH, APPROACH_QUEUE_SIZE);
    ad5761_write(CMD_WR_UPDATE_DAC_REG, current_z_position, DA_Z);
    while (1)
    {   
        // --> 1: Get into FAST mode
        if(status == 1){
            // Slider Begin, Fast Mode
            // forward 1 step, and read punch
            int punch = triangle_Wave_forward(1, 4095, 64);
            cformat_return_value(APPROACH_RETURN_PUNCH, punch, output, sizeof(output));
            UARTS_write(output);
            if(punch > cap_slow_limit){
                status = 5;
                ad5761_write(CMD_WR_UPDATE_DAC_REG, bias_voltage, DA_BIAS);
                // turn to Z scan mode
                cformat_return_value(APPROACH_RETURN_STATUS, status, output, sizeof(output));
                UARTS_write(output);
            }
            else if(punch > cap_fast_limit){
                status = 4;
                // turn to slow mode
                cformat_return_value(APPROACH_RETURN_STATUS, status, output, sizeof(output));
                UARTS_write(output);
            }
        }
        // --> 2: Get into Continous FORWARD mode
        else if(status == 2){
            int punch = triangle_Wave_forward(step, triangle_amplitude, triangle_slope);
            cformat_return_value(APPROACH_RETURN_PUNCH, punch, output, sizeof(output));
            UARTS_write(output);
            status = 0;
        }
        // --> 3: Get into Continous RETRACT mode
        else if(status == 3){
            triangle_Wave_backward(step, triangle_amplitude, triangle_slope);
            status = 0;
        }

        // --> 4: SLOW mode
        else if (status == 4)
        {   
            int punch = triangle_Wave_forward(1, triangle_amplitude, triangle_slope);
            cformat_return_value(APPROACH_RETURN_PUNCH, punch, output, sizeof(output));
            UARTS_write(output);
            if(punch > cap_slow_limit){
                status = 5;
                ad5761_write(CMD_WR_UPDATE_DAC_REG, bias_voltage, DA_BIAS);
                // turn to Z scan mode
                cformat_return_value(APPROACH_RETURN_STATUS, status, output, sizeof(output));
                UARTS_write(output);
            }
        }

        // --> 5: Z scan mode
        else if(status == 5){
            bool is_est = z_scan(target);
            if (!is_est)
            {   
                status = 4;
                // back to slow mode
                cformat_return_value(APPROACH_RETURN_STATUS, status, output, sizeof(output));
                UARTS_write(output);
            }
            else{
                status = 6;
                // turn to PID mode
                cformat_return_value(APPROACH_RETURN_STATUS, status, output, sizeof(output));
                UARTS_write(output);
            }
        }

        // -->: PID Mode
        else if(status == 6){
            // Read adc
            int read = adda_ad_write(ADS8689_NOP, 0, 0);
            read = adda_ad_write(ADS8689_NOP, 0, 0);
            // remapping the read value
            read = read - 32768;
            if(read < 0){
                read = -read;
            }
            // Execute PID
            int err = target - read;
            cformat_return_value(SYSTEM_GET_ADC, read, output, sizeof(output));
            UARTS_write(output);
            if(abs(err) > 400){
                // PID calculate
                int increase_step = (err*kp) + (err_acc * ki) + (err_last * kd);

                current_z_position = current_z_position + increase_step;
                // if scanner is out of range
                if (current_z_position > 65535){   
                    // set back to mode1
                    current_z_position = 0;
                    status = 4;
                    // turn to slow mode
                    cformat_return_value(APPROACH_RETURN_STATUS, status, output, sizeof(output));
                    UARTS_write(output);
                }
                else if(current_z_position < 0){
                    triangle_Wave_backward(10, triangle_amplitude, triangle_slope);
                    current_z_position = 0;
                    status = 4;
                    // turn to slow mode
                    cformat_return_value(APPROACH_RETURN_STATUS, status, output, sizeof(output));
                    UARTS_write(output);
                }
                else{
                    ad5761_write(CMD_WR_UPDATE_DAC_REG, current_z_position, DA_Z);
                }
                cformat_return_value(APPROACH_RETURN_PID, increase_step, output, sizeof(output));
                UARTS_write(output);
                err_acc = err_acc + err;
                err_last = err;
            }else{
                // clear PID parameters
                err_acc = 0;
                err_last = 0;
            }
        }

        vTaskDelay(1); 
        
        // queue receive
        uint32_t rcvBuffer = 0xF;
        xQueueReceive(approach_handle_queue, &(rcvBuffer), 0);

        u_int8_t command = rcvBuffer & 0xF;
        u_int16_t data = (rcvBuffer >> 4) & 0xFFFF;
        if (command == 0)
        {
            status = data;
            cformat_return_value(APPROACH_REGISTER, data, output, sizeof(output));
            UARTS_write(output);
        }
        else if(command == 1){
            step = data;
            cformat_return_value(APPROACH_SLIDER_STEP, data, output, sizeof(output));
            UARTS_write(output);
        }
        else if(command == 2){
            kp = data;
            kp = kp/10000;
            cformat_return_value(APPROACH_SET_KP, data, output, sizeof(output));
            UARTS_write(output);
        }
        else if(command == 3){
            ki = data;
            ki = ki/10000;
            cformat_return_value(APPROACH_SET_KI, data, output, sizeof(output));
            UARTS_write(output);
        }
        else if(command == 4){
            kd = data;
            kd = kd/10000;
            cformat_return_value(APPROACH_SET_KD, data, output, sizeof(output));
            UARTS_write(output);
        }
        else if(command == 5){
            target = data;
            target = target - 32768;
            if(target < 0){
                target = -target;
            }
            cformat_return_value(APPROACH_TARGET, target, output, sizeof(output));
            UARTS_write(output);
        }
        else if(command == 6){
            crash = data;
            crash = crash - 32768;
            if(crash < 0){
                crash = -crash;
            }
            cformat_return_value(APPROACH_CRASH, data, output, sizeof(output));
            UARTS_write(output);
        }
        else if(command == 7){
            triangle_amplitude = data;
            cformat_return_value(APPROACH_S_AMPLITUDE, data, output, sizeof(output));
            UARTS_write(output);
        }
        else if(command == 8){
            triangle_slope = data;
            cformat_return_value(APPROACH_S_SLOPE, data, output, sizeof(output));
            UARTS_write(output);
        }
        else if(command == 9){
            cap_fast_limit = data;
            cap_fast_limit = cap_fast_limit;
            cformat_return_value(APPROACH_S_FAST, cap_fast_limit, output, sizeof(output));
            UARTS_write(output);
        }
        else if(command == 10){
            cap_slow_limit = data;
            cap_slow_limit = cap_slow_limit;
            cformat_return_value(APPROACH_S_SLOW, cap_slow_limit, output, sizeof(output));
            UARTS_write(output);
        }
        else if(command == 11){
            // set bias voltage
            bias_voltage = data;
            ad5761_write(CMD_WR_UPDATE_DAC_REG, bias_voltage, DA_BIAS);
            cformat_return_value(APPROACH_BIAS, data, output, sizeof(output));
            UARTS_write(output);
        }
    }
    
}

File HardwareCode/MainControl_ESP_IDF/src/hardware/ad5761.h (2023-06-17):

// Reference: https://github.com/hellange/AD5761

#ifndef ad5761_h
#define ad5761_h

#include "driver/spi_master.h"
#include "driver/gpio.h"
#include "freertos/FreeRTOS.h"
#include "freertos/task.h"
#include "register.h"

// select SPI peripherals
#define AD5761_USED_SPI    SPI3_HOST

// select GPIO pins to used as SPI
#define AD5761_MOSI_PIN            23
#define AD5761_CLK_PIN             18

// define clock rate
#define AD5761_CLOCK_RATE 50000000

// define CS slect
#define csPin0  33
#define csPin1  25
#define csPin2  26
#define csPin3  27

void ad5761_pull_up_ss(char cs);
void ad5761_pull_down_ss(char cs);
void ad5761_init();
void ad5761_SPI_init();
void ad5761_write(uint8_t reg_addr_cmd, uint16_t reg_data, char cs);

#endif

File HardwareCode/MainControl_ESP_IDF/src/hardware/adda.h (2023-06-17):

// Reference: https://github.com/Helmuthn/ads8689_Arduino
// Reference: https://github.com/paulvha/AD57xx

#ifndef adda_h
#define adda_h

#include "driver/spi_master.h"
#include "driver/gpio.h"
#include "freertos/FreeRTOS.h"
#include "freertos/task.h"
#include "esp_log.h"
#include "register.h"
#include "uarthandle.h"

// select GPIO pins to used as SPI
#define ADDA_MOSI_PIN   13
#define ADDA_MISO_PIN   12
#define ADDA_CLK_PIN    14
#define DA_CS_PIN       32
#define AD_CS_PIN       4   

// select SPI peripherals
#define ADDA_USED_SPI    SPI2_HOST

// define clock rate
#define ADDA_CLOCK_RATE_AD 20000000
#define ADDA_CLOCK_RATE_DA 40000000

void adda_SPI_init();
void adda_init();
int adda_ad_write(uint8_t command, uint16_t address, uint16_t data);
void adda_12bitda_write(uint8_t reg_addr_cmd, uint16_t reg_data);


#endif

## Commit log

2022-06-16 2nd gen.
    [CopperStand.SLDPRT, DUMP_BALL.SLDPRT, PIEZO_FIX.SLDPRT, SampleTable.SLDPRT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]
2022-07-27 release 1.0.0
    [CopperStand.SLDPRT, DUMP_BALL.SLDPRT, PIEZO_FIX.SLDPRT, Spinner.SLDPRT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]
2022-07-27 stepper motor program
2023-09-04 file update
    [BOM_ControlBoard.xlsx, BOM_MCUBoard.xlsx, BOM_PowerBoard.xlsx, BOM_PreAmp.xlsx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]
2023-09-13 PCB file update
2023-09-21 Naming bug fix
    [PCB_Conncet.SLDPRT, PCB_Connect_component.SLDPRT, PZM_BASE.SLDPRT, PZM_BASE.STEP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]
2023-09-21 naming bug fix(upload)
    [Base.STEP, PCB_Conncet.SLDPRT, PCB_Connect_component.SLDPRT, PZM_BASE.SLDPRT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]
